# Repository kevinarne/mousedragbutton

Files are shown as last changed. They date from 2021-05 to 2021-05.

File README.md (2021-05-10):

# Single Button Keyboard
The goal for this is to make clicking and dragging easier for those that might have trouble doing that on a standard mouse. Press the button once and the mouse will press, press again and it will lift.

# Components
* Cherry MX (of your color choice), both PCB and panel mount work
* Keycap of your choice
* Arduino Pro Micro
* 3D printed enclosure (see stls directory)
* 22 AWG solid wire
* Micro USB cable
* 4 x #4-40 flat head screws, .25" long
* Piece of felt (optional)

# Needed Tools
* 3D printer (or access to one)
* Soldering iron
* Wire strippers
* Screw driver

# Theory of Operation
The keyboard uses an active low switch (an internal pullup resistor with the switch tied to ground) to trigger a change in state if enough time has passed since the last state toggle. When in a pressed state, the mouse button is held down, while in the unpressed state it is released. Debouncing is done through a simple delay calculation that can be tweaked if bouncing is detected.

# Assembly
* Press the switch into the square socket in the enclosure from the outside.
* Solder wires to one of the GND pins on the Pro Micro and another to the A3 pin. I recommend a few inches of wire, which can be trimmed after the Pro Micro is in place.
* Insert the micro USB end of the Pro Micro in the hole of the enclosure and snap the other end in place. Make sure to route the wires out through the gap in the socket for the Pro Micro.
* Solder the ends of the wire to the two terminals on the switch. It doesn't matter which one you connect each wire to, just make sure you don't connect them both to the same one.

# Programming
This project requires some way to flash the code to the Pro Micro. The easiest toolchain involves downloading the Arduino IDE and selecting the Leonardo board. You'll also need to select the port your Pro Micro is connected to, but there should only be one or two options. Resources for flashing the code are readily available on both Google and YouTube.

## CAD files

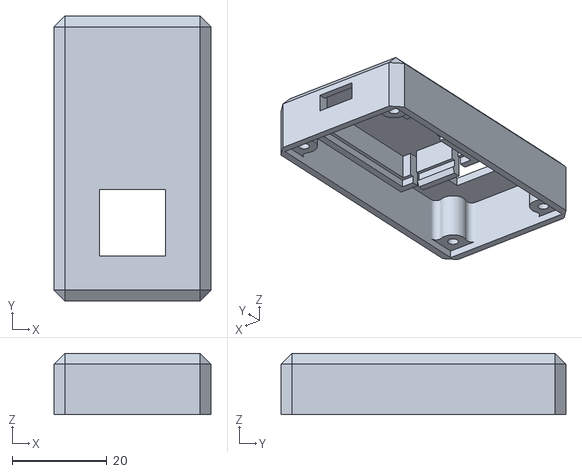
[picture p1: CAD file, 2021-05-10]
stl/enclosure.stl
33.0 x 60.0 x 12.9

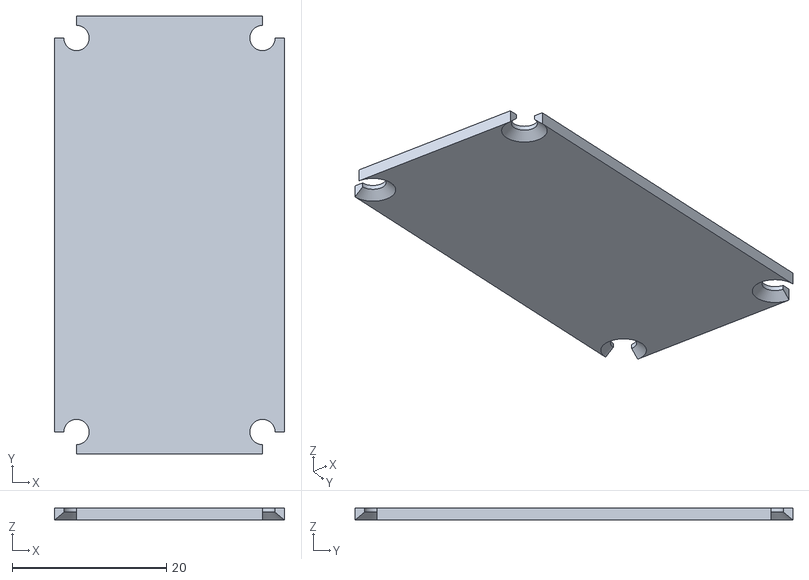
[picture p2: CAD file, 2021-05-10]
stl/cap.stl
29.8 x 56.8 x 1.59

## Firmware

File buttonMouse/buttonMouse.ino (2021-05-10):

#include <Mouse.h>

#define DEBOUNCE 140
#define BUTTON_PIN A3

boolean pressed = false;
long lastPressed = 0;
boolean stateToggled = false;

void setup() 
{
  Mouse.begin();
  pinMode(BUTTON_PIN, INPUT_PULLUP);
}

void loop() 
{
  boolean currentState = digitalRead(BUTTON_PIN); //Low means the button is pressed
  
  long timeSincePressed = millis() - lastPressed;
  
  if (!currentState && timeSincePressed > DEBOUNCE) //Switch ties the pin to ground, thus active low
  { 
      lastPressed = millis();
      pressed = !pressed; //Toggle state
      stateToggled = true;  //Flag that the state has changed
  }
  
  if(pressed && stateToggled)
  {
    Mouse.press();
    stateToggled = false;
  }
  if (pressed == false)
  {
    Mouse.release();
  }
}
